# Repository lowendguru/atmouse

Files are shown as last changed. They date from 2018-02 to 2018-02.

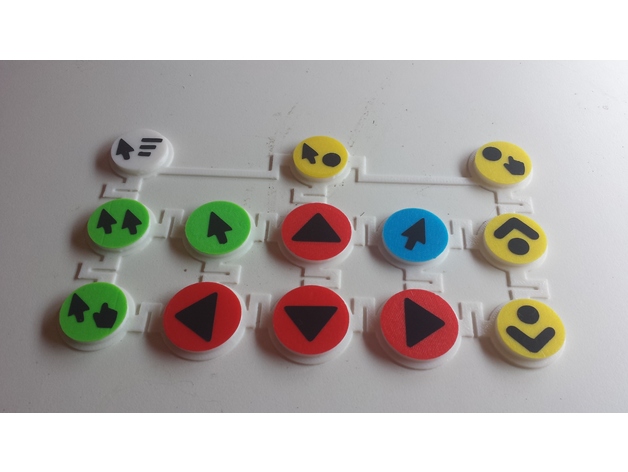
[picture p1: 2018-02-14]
pictures/59a67cc483de0d6e3dba985655f9e81f_preview_featured.jpg

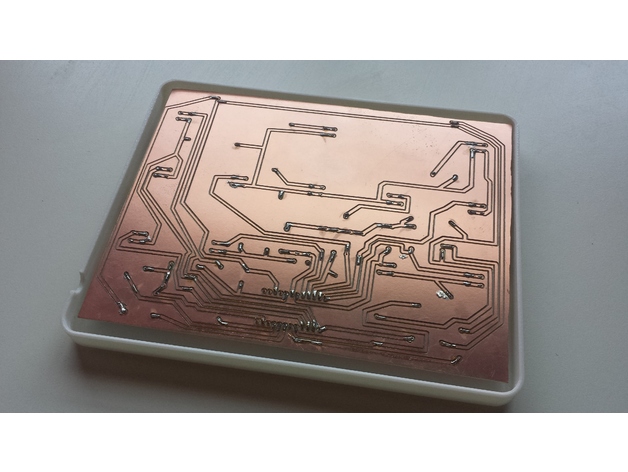
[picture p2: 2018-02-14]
pictures/8f39cfd2877d1b8f2fd800eb001ed761_preview_featured.jpg

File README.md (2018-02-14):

# Introduction to ATmouse

This device is intended to be an assistive technology solution for computer users whom due to disability or physical condition find it difficult to use a regular mouse but are still able to push buttons. Users with Parkinson's disease, any tremor related condition, cerebral palsy and many other conditions that interfere with the users' ability to make precise hand movements.

The device is based on the Arduino Pro Micro (Leonardo compatible) and thus is a plug and play input device, meaning that it will be recognized as a USB mouse without the need of any additional drivers.

The device has a total of 13 buttons and 3 LED lights. The user can press buttons to:
- Move the mouse pointer (up, down, left, right)
- Left click
- Double left click
- Right click
- Hold left click
- Middle button click
- Hold middle button click
- Scroll wheel (up and down)
- Change the mouse movement speed between 3 different settings.

# Instructions

Print the 3 plastic parts (front case, back case, buttons array).
Etch or mill the PCB. This is a single sided PCB board and the tracks only use the "bottom" layer. Ignore the "top" layer of the Eagle design, but use wire jumpers to make the connections seen in the "top" layers.
Solder all electrical components to the PCB according to the Eagle design.
Upload the .ino sketch to the Pro Mini using Arduino IDE (Leonardo board settings).

Assemble the device. Start by placing the cover facing down on a table.
Then put the buttons array inside the sockets.
Make sure the USB cable is connected to the Pro Micro. Then place the PCB, the 5mm LEDs will fit inside their sockets and this will align the whole board into the front case.
Finally place the back case to close. You may have to glue the back case (as there are no screw holes in this version).
Optionally, you can use some pieces Polyurethane foam or similar material between the buttons array and the PCB, and also between the PCB and the back case for a tighter fit.

# Bill of materials

13 - 6mm push buttons
13 - 10k resistors
3 - 5mm LED
3 - 1k resistors
1 - PCB board 200x150mm (1 sided)
1 - Arduino Pro Micro
1 - Mini-USB cable
1 - Front case (3d printed)
1 - Back case (3d printed)
1 - Buttons array (3d printed)
Some foam rubber, Polyurethane foam or similar material (for a tighter fit)
Some strong glue (no screws yet, sorry)

# Demo video

https://www.youtube.com/watch?v=QU9dcgiuyGs

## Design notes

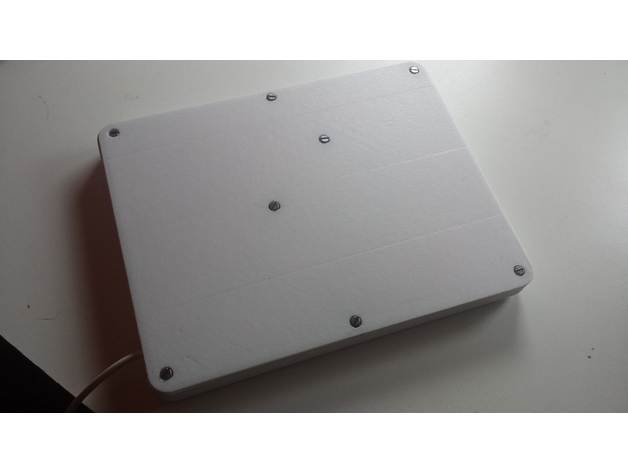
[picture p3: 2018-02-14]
pictures/ea3a17e51f395046b7e23d7d19805bd4_preview_featured.jpg

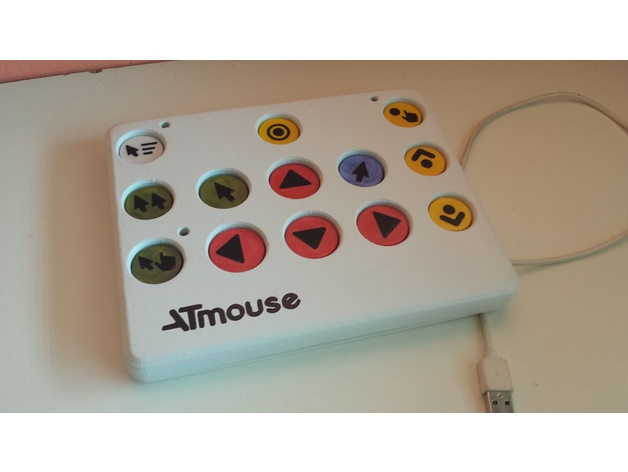
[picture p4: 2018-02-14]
pictures/62d5ee24b28fbe57dd52866ed5d5ac9a_preview_featured.jpg

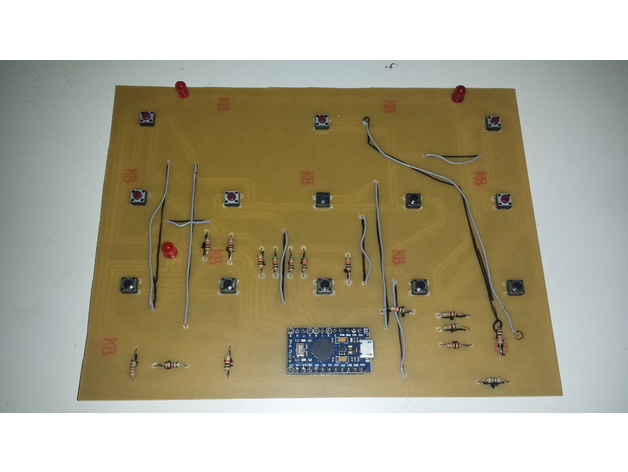
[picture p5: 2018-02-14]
pictures/91fcb61a9fc78a9e5922dd8a7438702f_preview_featured.jpg

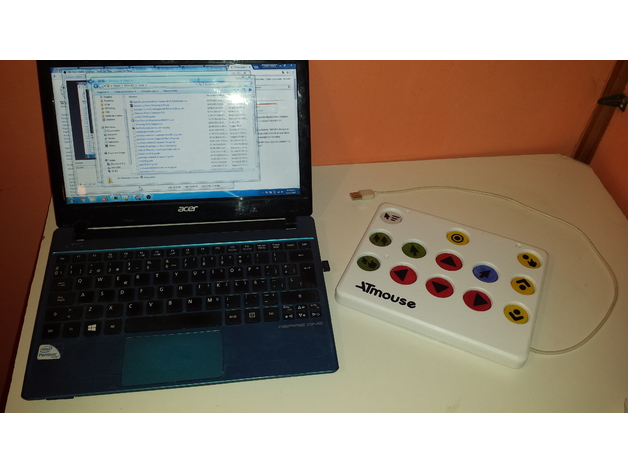
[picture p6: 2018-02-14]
pictures/262c6cef5a1a5fbf4d7a4019c271f640_preview_featured.jpg

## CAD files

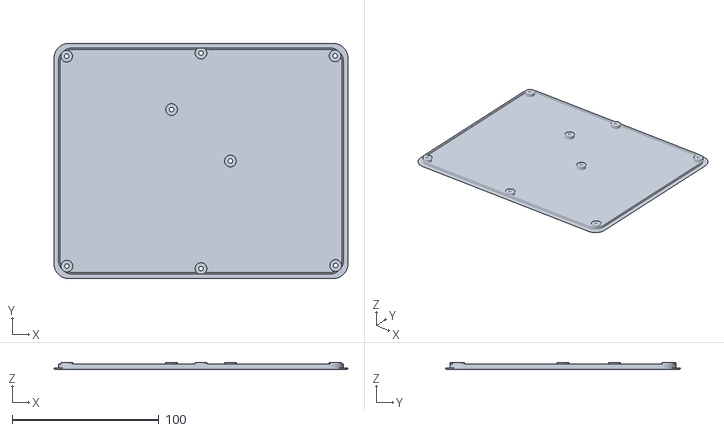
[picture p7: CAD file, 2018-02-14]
stl/back_v5.stl
200.0 x 160.0 x 5.00

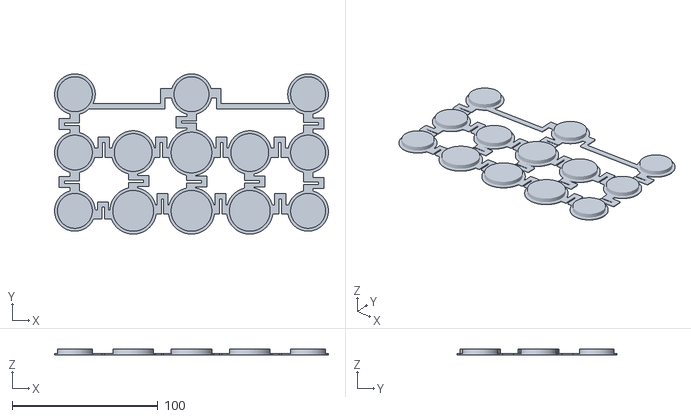
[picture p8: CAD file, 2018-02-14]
stl/buttons_v4.stl
188.0 x 110.0 x 4.00

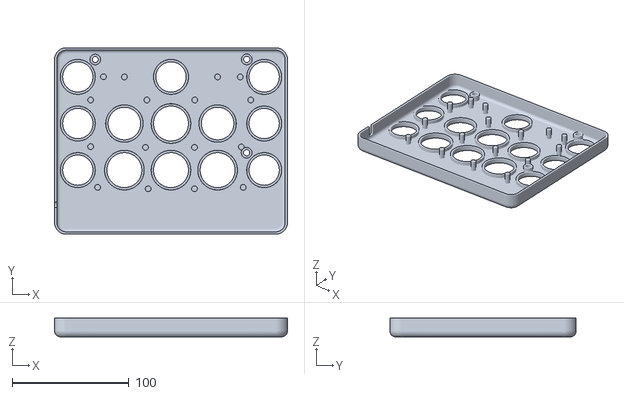
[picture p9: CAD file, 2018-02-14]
stl/front_v4.stl
200.0 x 160.0 x 16.0

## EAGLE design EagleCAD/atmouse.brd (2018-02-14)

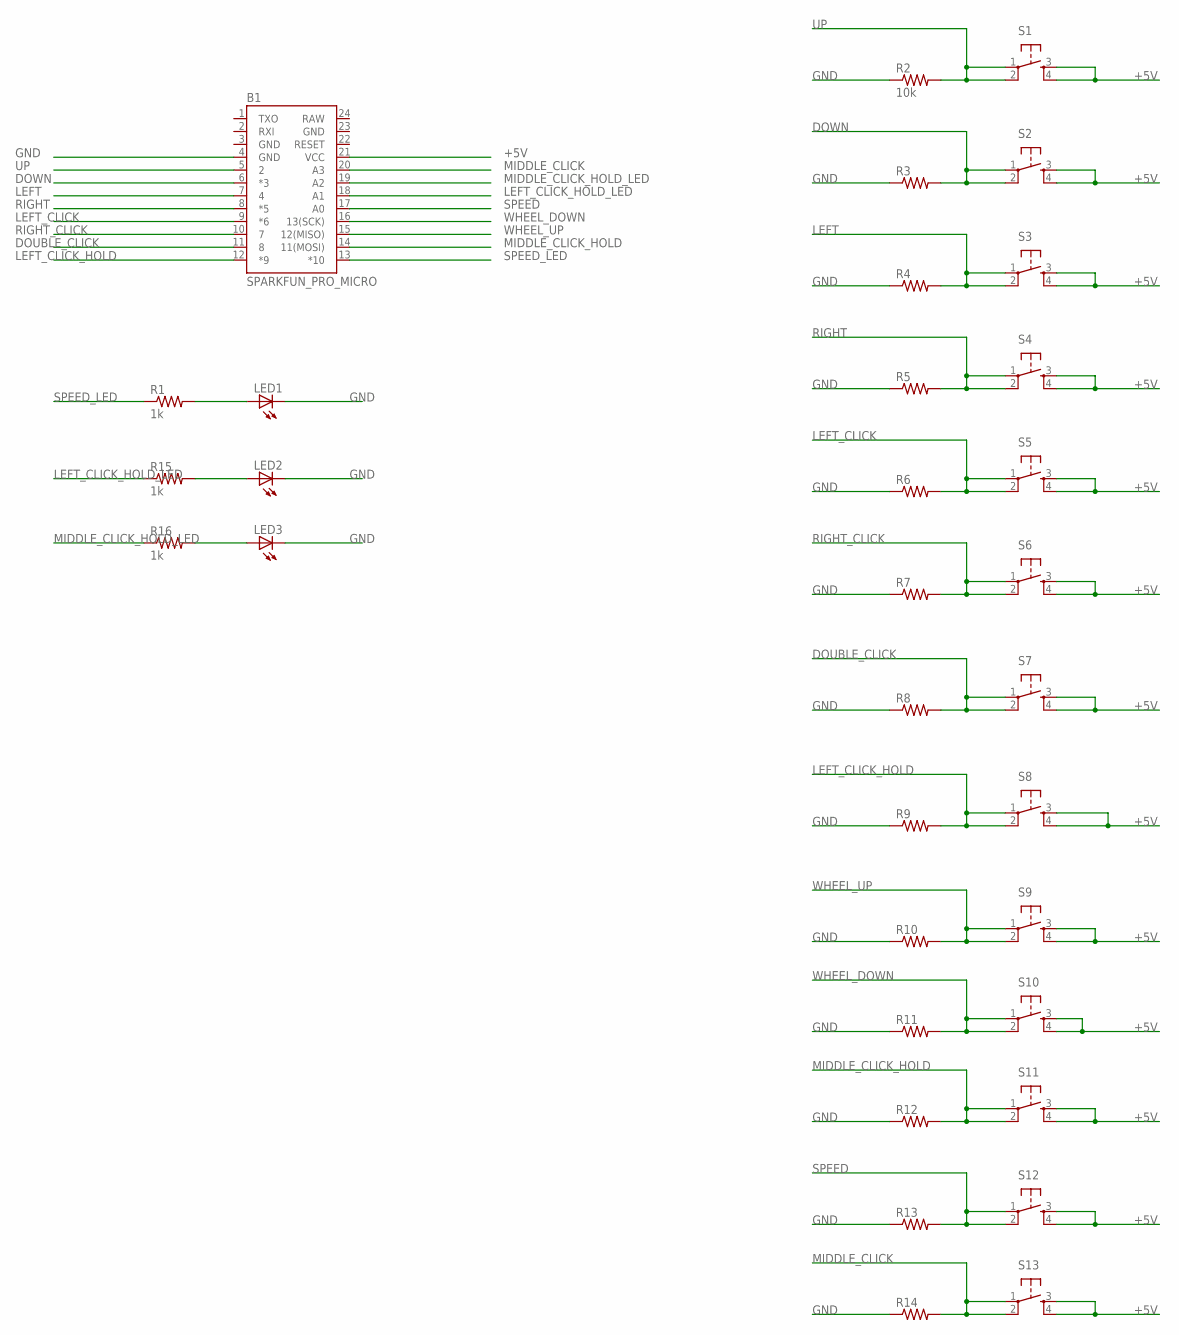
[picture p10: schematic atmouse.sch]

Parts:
B1: SPARKFUN_PRO_MICRO
LED1, LED2, LED3: LED5MM
R1, R15, R16: 1k; AXIAL-0.5
R2: 10k; AXIAL-0.5
R3, R4, R5, R6, R7, R8, R9, R10, R11, R12, R13, R14: RESISTORPTH-1/2W; AXIAL-0.5
S1, S2, S3, S4, S5, S6, S7, S8, S9, S10, S11, S12, S13: TAC_SWITCHPTH; TACTILE-PTH

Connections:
+5V: B1.21 (VCC), S1.3, S1.4, S2.3, S2.4, S3.3, S3.4, S4.3, S4.4, S5.3, S5.4, S6.3, S6.4, S7.3, S7.4, S8.3, S8.4, S9.3, S9.4, S10.3, S10.4, S11.3, S11.4, S12.3, S12.4, S13.3, S13.4
DOUBLE_CLICK: B1.11 (8), R8.P$2 (2), S7.1, S7.2
DOWN: B1.6 (*3), R3.P$2 (2), S2.1, S2.2
GND: B1.3 (GND), B1.4 (GND), B1.23 (GND), LED1.K (C), LED2.K (C), LED3.K (C), R2.P$1 (1), R3.P$1 (1), R4.P$1 (1), R5.P$1 (1), R6.P$1 (1), R7.P$1 (1), R8.P$1 (1), R9.P$1 (1), R10.P$1 (1), R11.P$1 (1), R12.P$1 (1), R13.P$1 (1), R14.P$1 (1)
LEFT: B1.7 (4), R4.P$2 (2), S3.1, S3.2
LEFT_CLICK: B1.9 (*6), R6.P$2 (2), S5.1, S5.2
LEFT_CLICK_HOLD: B1.12 (*9), R9.P$2 (2), S8.1, S8.2
LEFT_CLICK_HOLD_LED: B1.18 (A1), R15.P$1 (1)
MIDDLE_CLICK: B1.20 (A3), R14.P$2 (2), S13.1, S13.2
MIDDLE_CLICK_HOLD: B1.14 (11(MOSI)), R12.P$2 (2), S11.1, S11.2
MIDDLE_CLICK_HOLD_LED: B1.19 (A2), R16.P$1 (1)
unnamed: LED1.A, R1.P$2 (2)
unnamed: LED2.A, R15.P$2 (2)
unnamed: LED3.A, R16.P$2 (2)
RAW: B1.24 (RAW)
RIGHT: B1.8 (*5), R5.P$2 (2), S4.1, S4.2
RIGHT_CLICK: B1.10 (7), R7.P$2 (2), S6.1, S6.2
SPEED: B1.17 (A0), R13.P$2 (2), S12.1, S12.2
SPEED_LED: B1.13 (*10), R1.P$1 (1)
UP: B1.5 (2), R2.P$2 (2), S1.1, S1.2
WHEEL_DOWN: B1.16 (13(SCK)), R11.P$2 (2), S10.1, S10.2
WHEEL_UP: B1.15 (12(MISO)), R10.P$2 (2), S9.1, S9.2

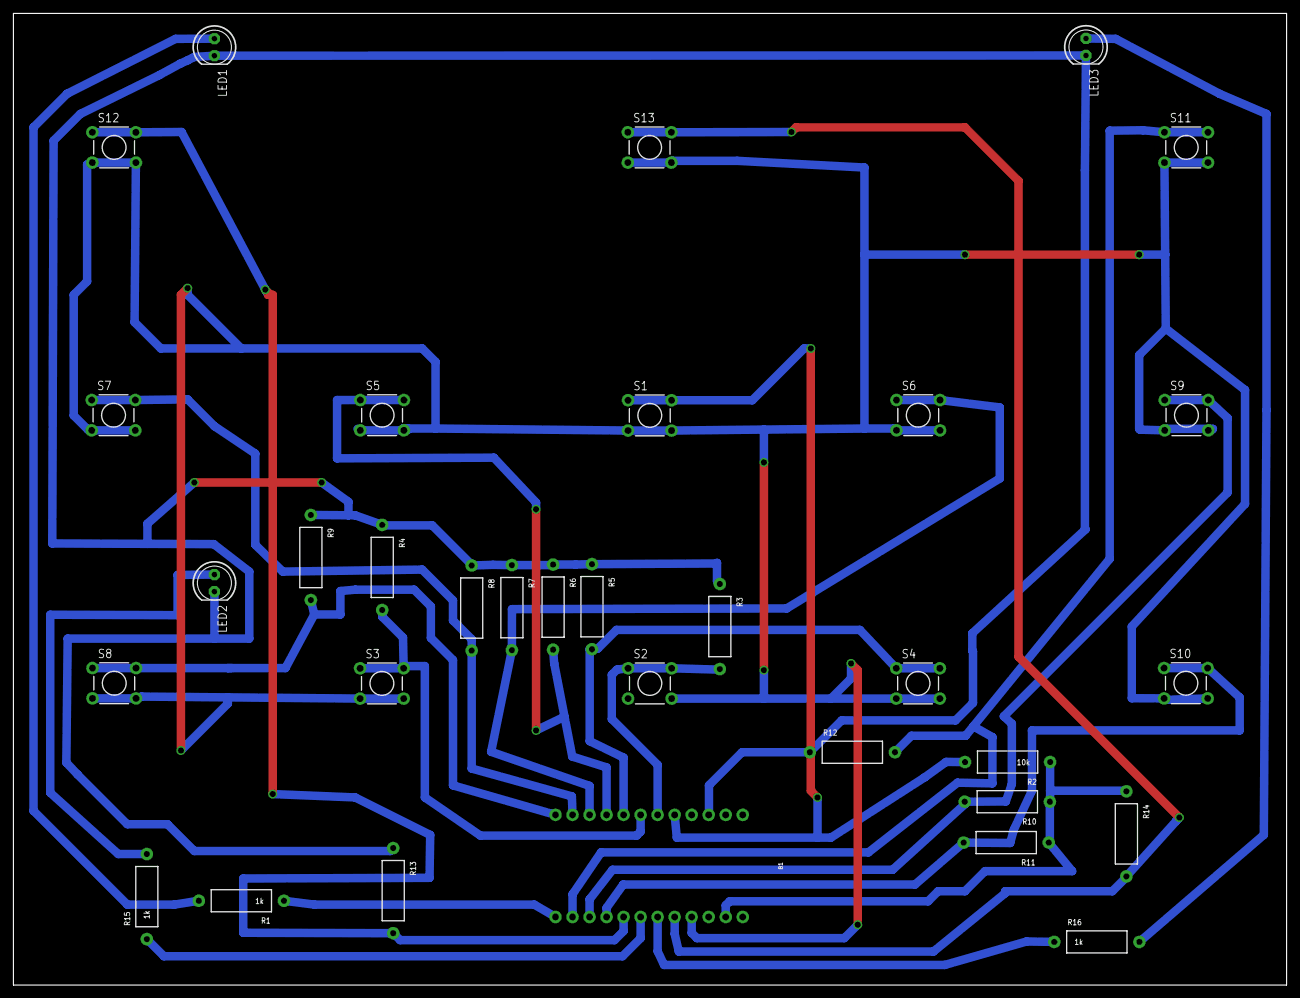
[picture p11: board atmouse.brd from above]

Board: 2 copper layers, 190.0 x 145.0 mm, 33 parts (0 on the bottom side), 21 nets.

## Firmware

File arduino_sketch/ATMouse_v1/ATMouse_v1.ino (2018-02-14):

#include "Mouse.h"

// set pin numbers for the five buttons:
const int upButton = 2;
const int downButton = 3;
const int leftButton = 4;
const int rightButton = 5;
const int leftClickButton = 6;
const int rightClickButton = 7;
const int doubleClickButton = 8;
const int leftClickHoldButton = 9;
const int middleClickButton = A3;
const int wheelUpButton = 14;
const int wheelDownButton = 15;
const int middleClickHoldButton = 16;
const int speedButton = A0;
const int leftClickHoldLED = A1;
const int middleClickHoldLED = A2;
const int speedLED = 10;
const int speedLedValueLow = 30;
const int speedLedValueMid = 125;
const int speedLedValueHigh = 255;


unsigned long leftClickDebouncer = 0;
unsigned long rightClickDebouncer = 0;
unsigned long middleClickDebouncer = 0;
unsigned long doubleClickDebouncer = 0;
unsigned long leftClickHoldDebouncer = 0;
unsigned long middleClickHoldDebouncer = 0;
unsigned long speedDebouncer = 0;
bool isLeftClickHold = false;
bool isMiddleClickHold = false;

int speedValue = 1;


int range = 2;              // output range of X or Y movement; affects movement SPEED
int responseDelay = 10;     // response delay of the mouse, in ms


void setup() {
  // initialize the buttons' inputs:
  pinMode(upButton, INPUT);
  pinMode(downButton, INPUT);
  pinMode(leftButton, INPUT);
  pinMode(rightButton, INPUT);
  pinMode(leftClickButton, INPUT);

  pinMode(rightClickButton, INPUT);
  pinMode(doubleClickButton, INPUT);
  pinMode(leftClickHoldButton, INPUT);
  pinMode(middleClickButton, INPUT);
  pinMode(wheelUpButton, INPUT);
  pinMode(wheelDownButton, INPUT);
  pinMode(middleClickHoldButton, INPUT);

  pinMode(speedButton, INPUT);
  pinMode(leftClickHoldLED, OUTPUT);
  pinMode(middleClickHoldLED, OUTPUT);
  pinMode(speedLED, OUTPUT);


  //TODO poner flashes de LED para indicar inicializacion
  digitalWrite(leftClickHoldLED, LOW);
  digitalWrite(middleClickHoldLED, LOW);
  digitalWrite(speedLED, LOW);

  analogWrite(speedLED, speedLedValueLow);

  
  // initialize mouse control:
  Mouse.begin();
}

void loop() {
  // read the buttons:
  int upState = digitalRead(upButton);
  int downState = digitalRead(downButton);
  int rightState = digitalRead(rightButton);
  int leftState = digitalRead(leftButton);
  int leftClickState = digitalRead(leftClickButton);

  int rightClickState = digitalRead(rightClickButton);
  int doubleClickState = digitalRead(doubleClickButton);
  int leftClickHoldState = digitalRead(leftClickHoldButton);
  int middleClickState = digitalRead(middleClickButton);
  int wheelUpState = digitalRead(wheelUpButton);
  int wheelDownState = digitalRead(wheelDownButton);
  int middleClickHoldState = digitalRead(middleClickHoldButton);
  int speedState = digitalRead(speedButton);



  // MOVEMENT
  // TODO el wheeldistance esta un poco demasiado rapido
  // calculate the movement distance based on the button states:
  int  xDistance = (rightState - leftState) * range;
  int  yDistance = ( downState - upState) * range;
  int  wheelDistance = ( wheelUpState - wheelDownState) ;

  // if X or Y is non-zero, move:
  if ((xDistance != 0) || (yDistance != 0) || wheelDistance != 0) {
    Mouse.move(xDistance, yDistance, wheelDistance);
  }
  

  //CLICKS

 // LEFT CLICK BUTTON
  if (leftClickState && leftClickDebouncer < millis()) {
     Mouse.press(MOUSE_LEFT);
     leftClickDebouncer = millis() + 10;
  } else if(!leftClickState && !isLeftClickHold){
     Mouse.release(MOUSE_LEFT);
  }
  
 // RIGHT CLICK BUTTON
  if (rightClickState && rightClickDebouncer < millis()) {
     Mouse.press(MOUSE_RIGHT);
     rightClickDebouncer = millis() + 10;
  } else if(!rightClickState){
     Mouse.release(MOUSE_RIGHT);
  }
 
  
 // DOUBLE LEFT CLICK
 if(doubleClickState && doubleClickDebouncer < millis()){
    Mouse.click(MOUSE_LEFT);
    delay(20);
    Mouse.click(MOUSE_LEFT);
    doubleClickDebouncer = millis() + 1000;
  } 

  
  // LEFT CLICK HOLD
  if(leftClickHoldState && leftClickHoldDebouncer < millis()){
    if(!isLeftClickHold){
      isLeftClickHold = true;
      Mouse.press(MOUSE_LEFT);
      digitalWrite(leftClickHoldLED, HIGH);
      leftClickHoldDebouncer = millis() + 1000;
    } else {
      isLeftClickHold = false;
      Mouse.release(MOUSE_LEFT);
      digitalWrite(leftClickHoldLED, LOW);
      leftClickHoldDebouncer = millis() + 1000;
    } 
  }

 // MIDDLE CLICK BUTTON
  if (middleClickState && middleClickDebouncer < millis()) {
     Mouse.click(MOUSE_MIDDLE);
     middleClickDebouncer = millis() + 200;
  }

  // MIDDLE CLICK HOLD
  if(middleClickHoldState && middleClickHoldDebouncer < millis()){
    if(!isMiddleClickHold){
      isMiddleClickHold = true;
      Mouse.press(MOUSE_MIDDLE);
      digitalWrite(middleClickHoldLED, HIGH);
      middleClickHoldDebouncer = millis() + 1000;
    } else {
      isMiddleClickHold = false;
      Mouse.release(MOUSE_MIDDLE);
      digitalWrite(middleClickHoldLED, LOW);
      middleClickHoldDebouncer = millis() + 1000;
    } 
  }

  // SPEED CONTROL
  if(speedState && speedDebouncer < millis()){
    switch (speedValue){
      case 1:
        speedValue = 2;
        range = 5;
        analogWrite(speedLED, speedLedValueMid);
        break;
      case 2:
        speedValue = 3;
        range = 7;
        digitalWrite(speedLED, HIGH);
        break;
      case 3:
        speedValue = 1;
        range = 2;
        analogWrite(speedLED, speedLedValueLow);
        break;
    }

    speedDebouncer = millis() + 300;
  }
  

  // a delay so the mouse doesn't move too fast:
  delay(responseDelay);
}

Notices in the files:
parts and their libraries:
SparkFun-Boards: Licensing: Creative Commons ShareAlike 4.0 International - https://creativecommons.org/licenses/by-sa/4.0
